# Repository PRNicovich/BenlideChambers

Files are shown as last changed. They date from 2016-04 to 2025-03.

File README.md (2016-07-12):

Benlide imaging chambers

Files and design instructions for 3D printed imaging chambers.

Work done by Ben Goodnow for EMBL Australia Node in Single Molecule Science at UNSW in conjunction with Rusty Nicovich and Kat Gaus.

PDF goes into more detail on comparison of these chambers to the commercially-available ones, as well as design rationale.  

Assembly instructions included in AssemblyNotes.txt.  For a single chamber, print off the base, main, and cover (optional) STL files.  Laser cut corresponding gasket. Then glue in magnets and you're ready to go!

Solidworks files available upon request (p.nicovich@unsw.edu.au).

End result - an imaging chamber that performs at least as well as a commercial one for microscopy for 1/50th the cost. 

New chambers are being added as we develop them.  These include new coverslip sizes as well as specialized applications, such as simultaneous imaging and electrochem manipulation.

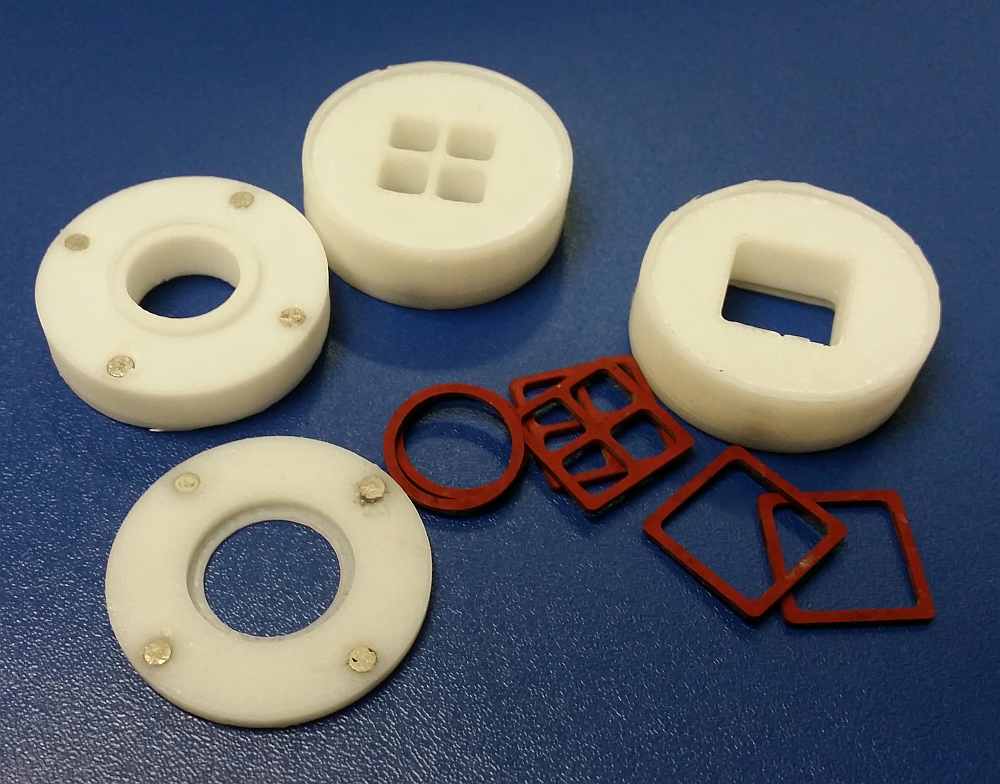
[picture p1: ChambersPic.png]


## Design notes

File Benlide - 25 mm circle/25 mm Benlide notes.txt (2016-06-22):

STL files are for two parts of chamber for 25 mm round coverslips. 

DXF file is for gasket for 25 mm round coverslips. 

Chamber parts require addition of 3 mm x 1 mm round Nd magnets.  These were sourced from similar vendors as given in master project instructions.  16 x N35 magnets required for each chamber.  Magnets are held in place with two-part epoxy.  Ensure that all magnets have the same North-South orientation so top and bottom rotational orientation is unimportant.  Check that any stray filament is removed from magnet recesses in print so that magnets can sit flush or just below the printed surface of the part.

Gasket is laser-cut from 1.25 mm thick silicone rubber sheet.  Material sourced from same vendor as given in master project instructions.

Care and some testing must be taken to ensure tolerances are met for a good seal with coverslip without excessive force and cracking.  Most critical dimension is the height of the recess in which the gasket rests on the chamber top.  If this is too tall there will not be a good seal; too short and there may be excessive force on the coverslip or poor binding between the top and bottom.  Also, top and bottom should have a good slip fit on their own.  This may require some adjustment of the diameter of the mating parts depending on the nozzle diameter and printer kerf if a different printer is used.

Printed on Zortrax M200 w/ Z-UltraT filament, 0.09 mm layer height, and medium infill.  As mentioned, some dimensions of the parts may need to be adjusted for different printers.  Each part is oriented on the print bed so that the magnet side is upright.  This prints the parts with no support material.  With a heated bed multiple parts can be printed at one time, otherwise single-part runs is recommended to avoid warping.

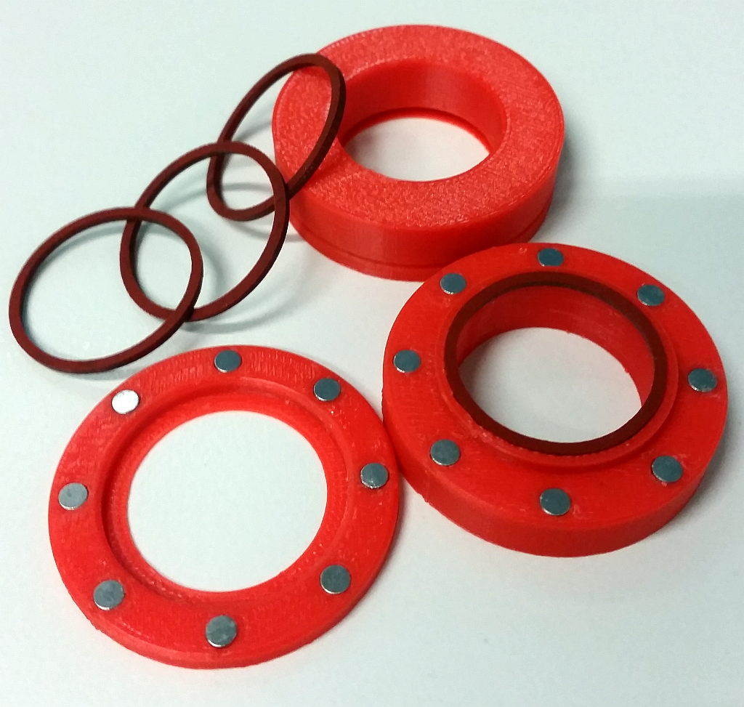
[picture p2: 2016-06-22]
Benlide - 25 mm circle/25 mm Benlide.png

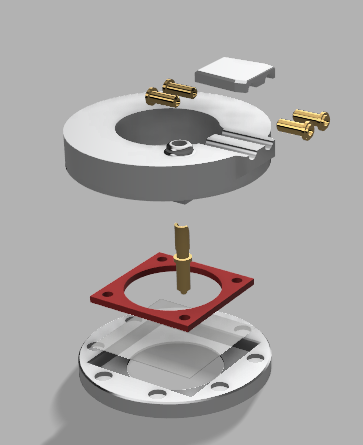
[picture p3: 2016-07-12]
ElectroBenlide/ElectroLideExplode.png

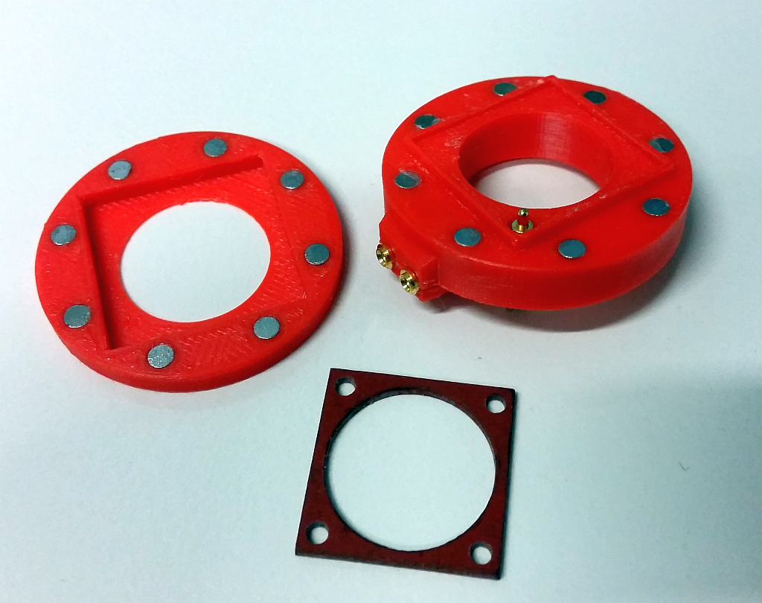
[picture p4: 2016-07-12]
ElectroBenlide/ElectroLide.png

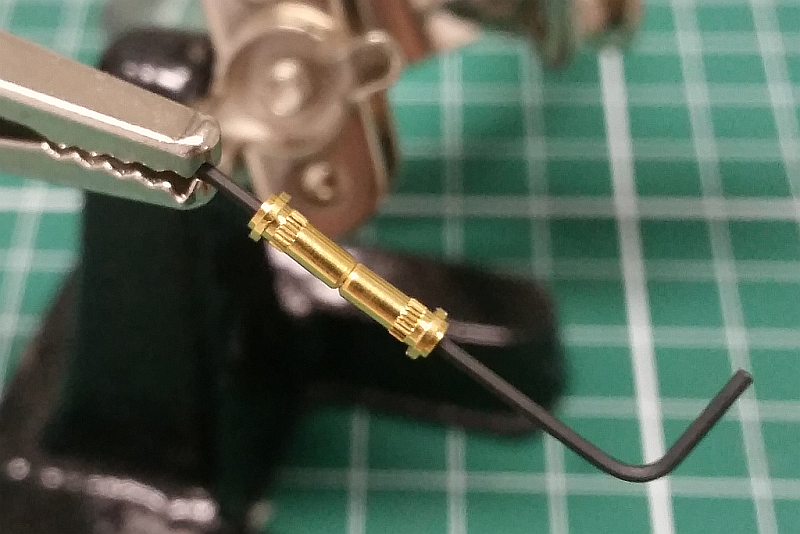
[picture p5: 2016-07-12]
ElectroBenlide/PCBSocketsOnStringer.png

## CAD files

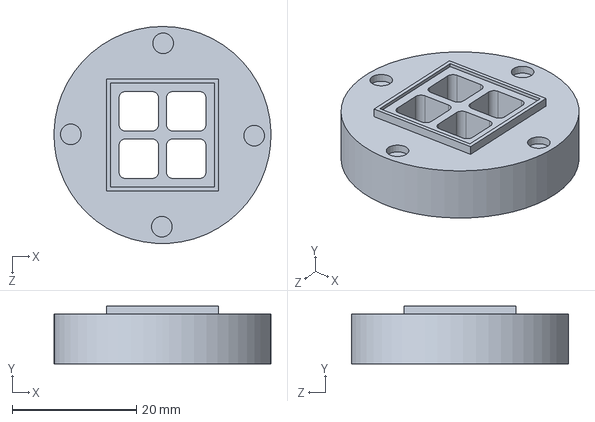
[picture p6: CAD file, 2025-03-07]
Benlide - Multi/CAD/MultiMain.SLDPRT
35.0 x 9.30 x 35.0 mm

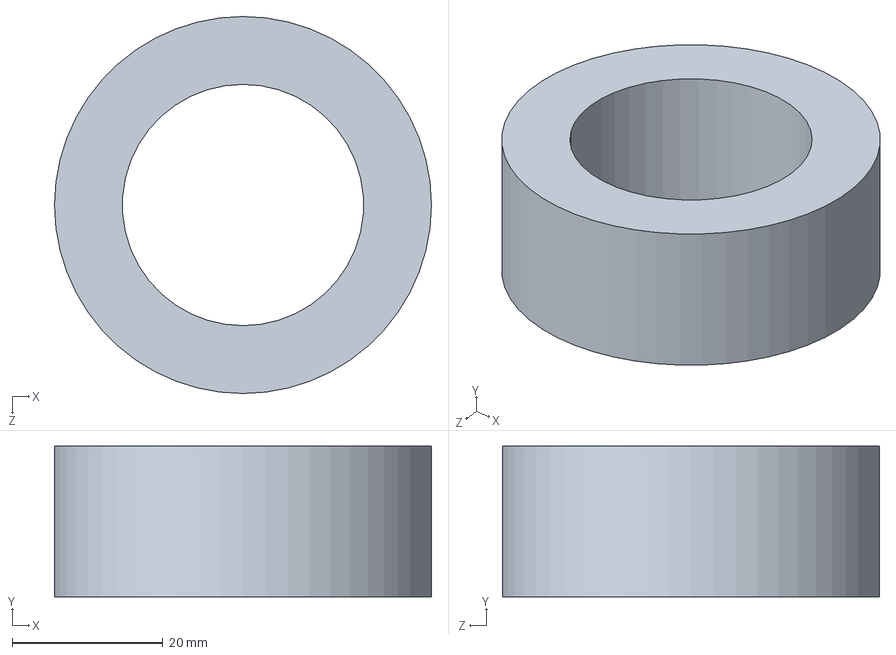
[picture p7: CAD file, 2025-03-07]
ProtoTest/CAD/Main Body.SLDPRT
50.0 x 20.0 x 50.0 mm

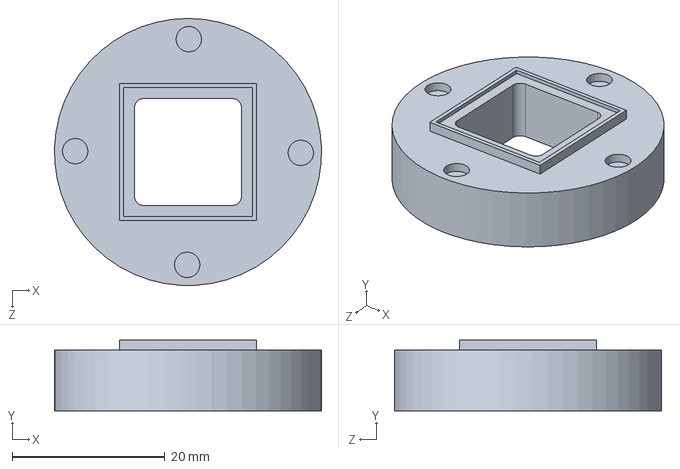
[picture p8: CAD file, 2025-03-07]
Benlide - 18 mm Square/CAD/SquareMain.SLDPRT
35.0 x 9.30 x 35.0 mm

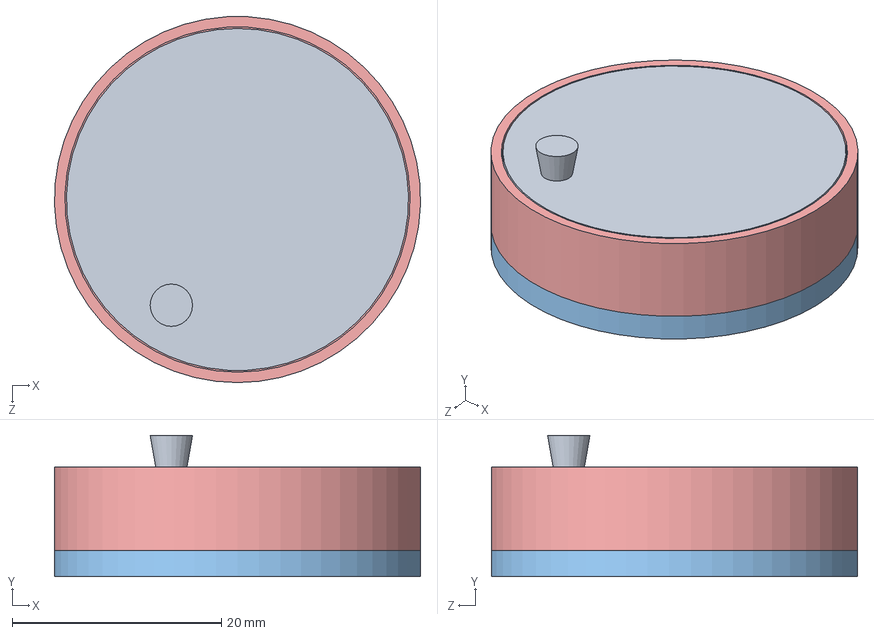
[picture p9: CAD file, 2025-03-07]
Benlide - 25 mm circle/CAD/Circle Assembly.SLDASM
35.0 x 13.5 x 35.0 mm
CircleGasket
CircleBase
CircleCoverslip
CircleMain
DiskMagnet x 8

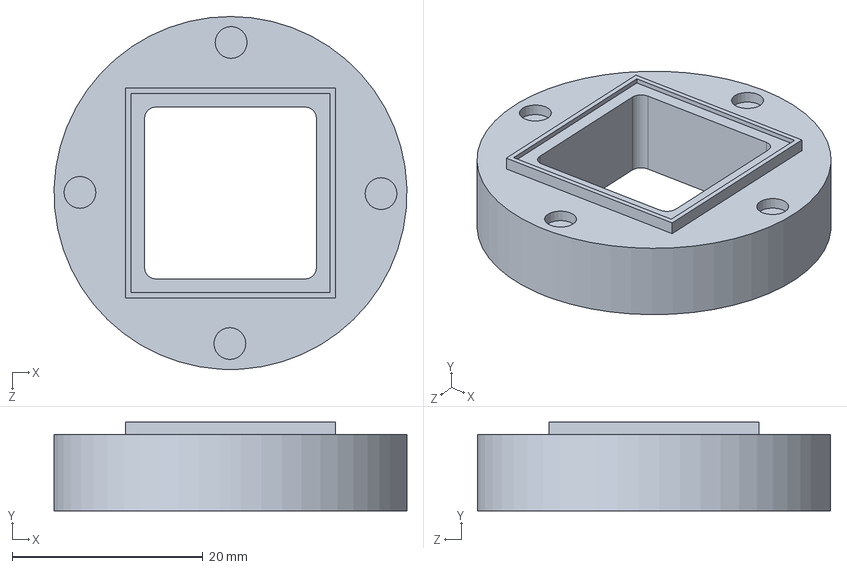
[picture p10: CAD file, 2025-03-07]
Benlide - Square - 22mm/CAD/SquareMain22.SLDPRT
37.0 x 9.30 x 37.0 mm

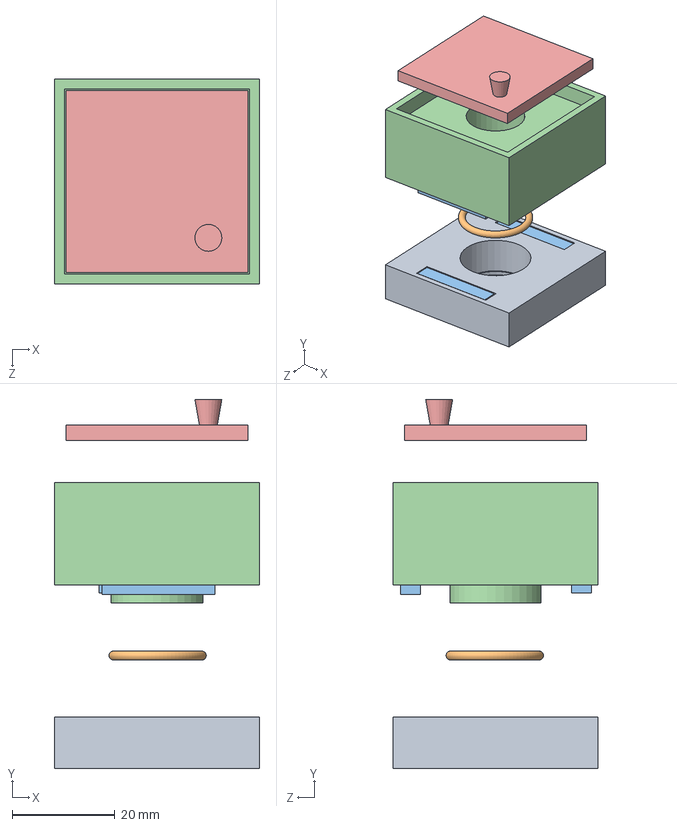
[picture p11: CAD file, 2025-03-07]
ProtoTest/CAD/Chamlide Assembly.SLDASM
40.0 x 72.0 x 40.0 mm
Bottom Plate
O-Ring
Magnet x 4
MainBod
TopCover^Chamlide Assembly

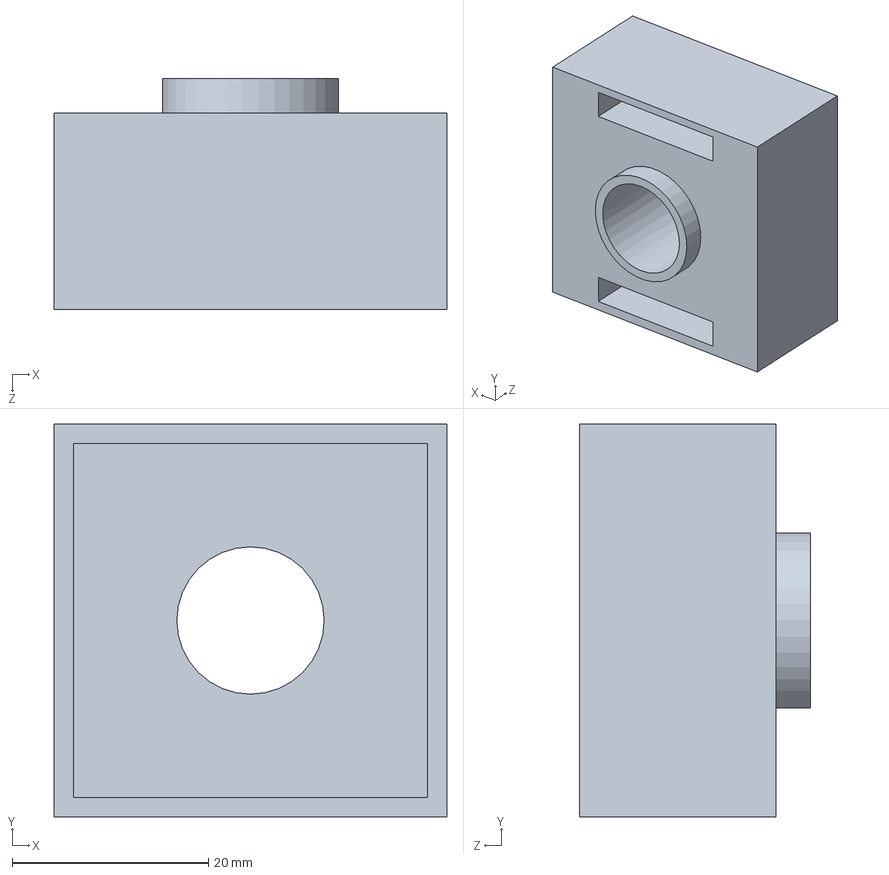
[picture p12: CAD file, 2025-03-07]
ProtoTest/CAD/MainBod.sldprt
40.0 x 40.0 x 23.5 mm

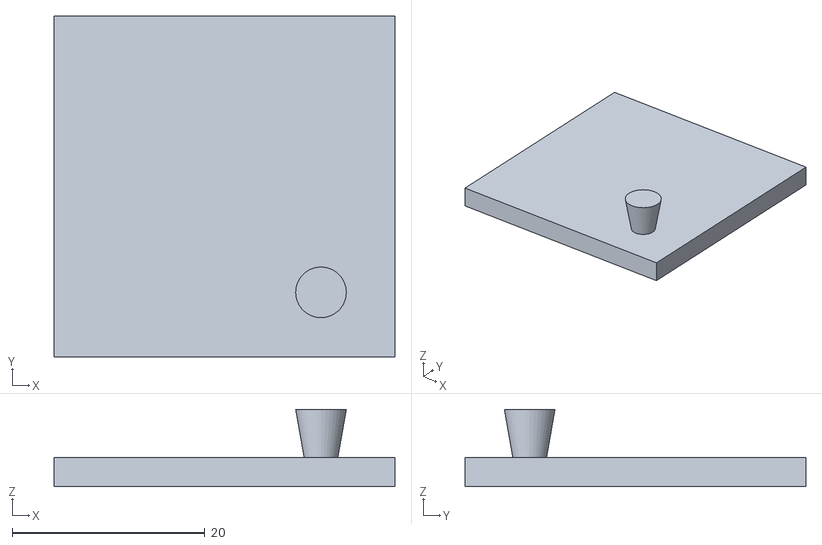
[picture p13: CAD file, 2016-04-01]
ProtoTest/CAD/TopCover^Chamlide Assembly.STL
35.4 x 35.4 x 8.00

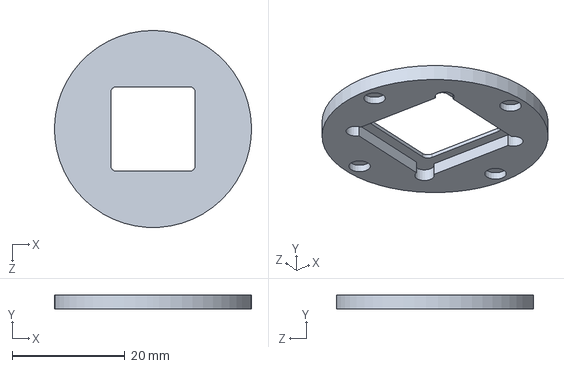
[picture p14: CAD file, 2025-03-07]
Benlide - 18 mm Square/CAD/SquareBase.sldprt
35.0 x 2.50 x 35.0 mm

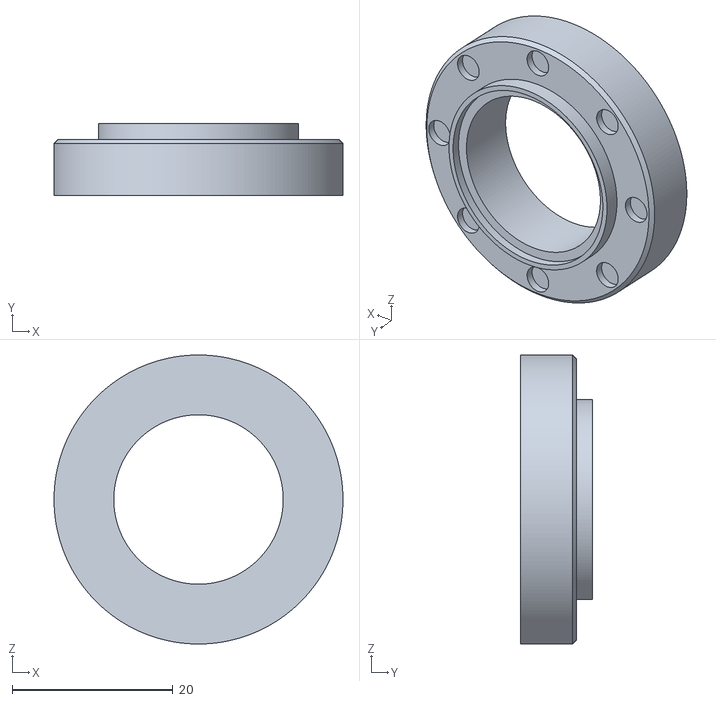
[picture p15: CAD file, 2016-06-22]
Benlide - 25 mm circle/25 mm top.stl
36.0 x 9.00 x 36.0

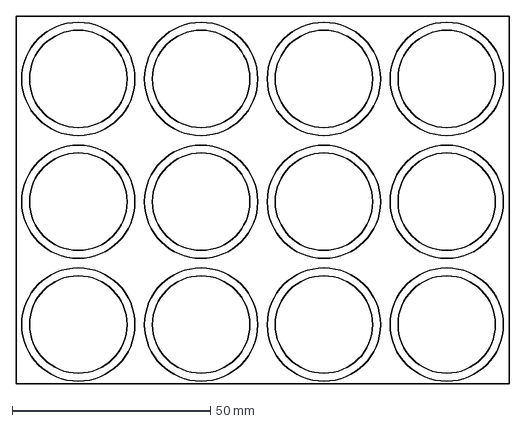
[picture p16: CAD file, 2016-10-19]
Benlide - 30 mm circle/30mmBenlideGasket.dxf
124.5 x 92.9 mm

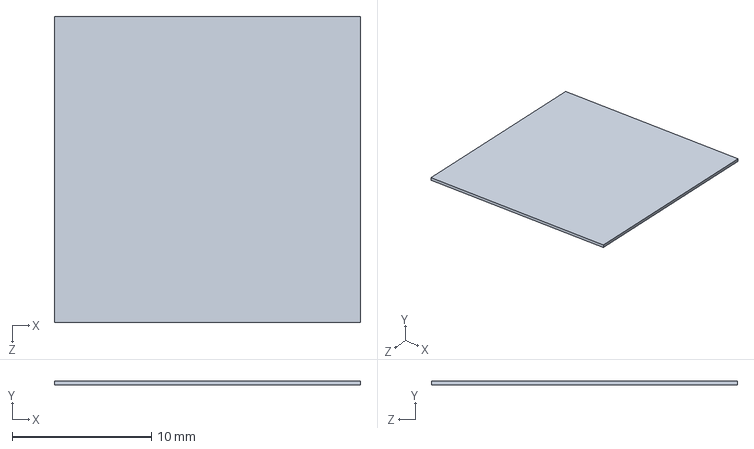
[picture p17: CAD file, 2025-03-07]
Benlide - Square - 22mm/CAD/SquareCoverslip22.sldprt
22.0 x 0.3 x 22.0 mm

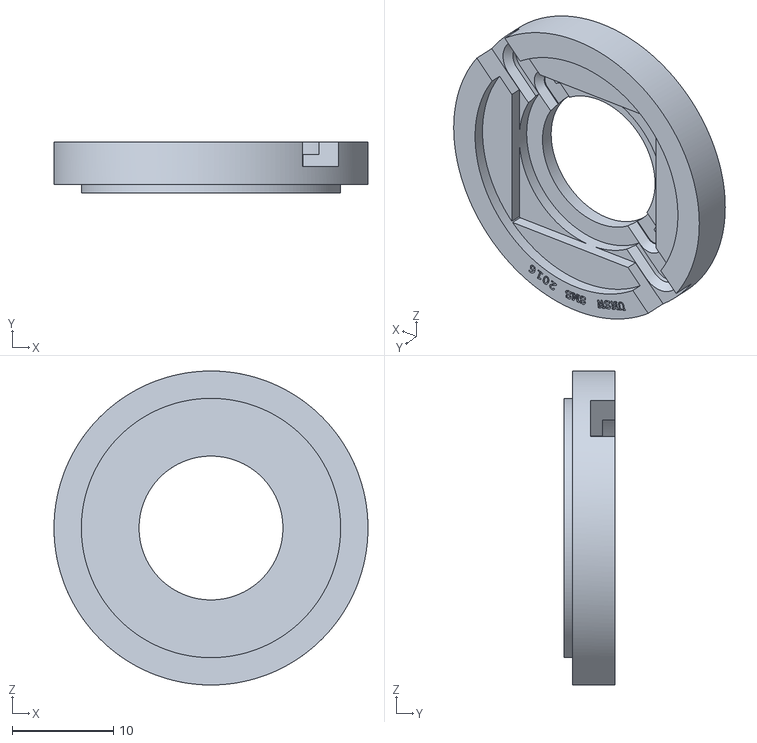
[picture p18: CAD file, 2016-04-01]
Coverslip Holder/CoverslipHolder18rnd18sq25sq.stl
31.0 x 5.00 x 31.0

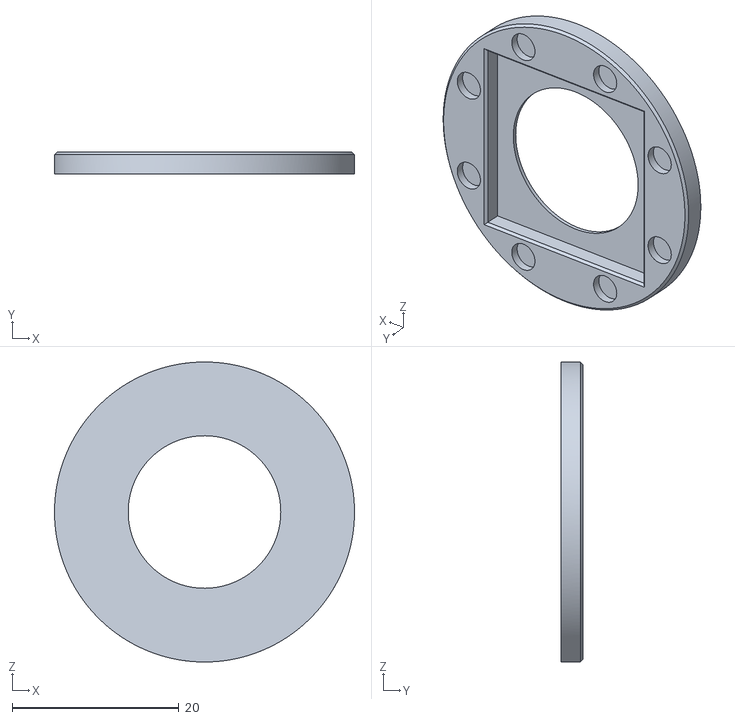
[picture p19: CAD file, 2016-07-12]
ElectroBenlide/ElectroLideBottom.stl
36.0 x 2.60 x 36.0

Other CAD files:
Benlide - 25 mm circle/CAD/CircleMain.SLDPRT
Benlide - 25 mm circle/CAD/CircleBase.sldprt
Laser Print Gasket/CAD/CircleGasket18mm.SLDPRT
Benlide - 18 mm Square/CAD/SquareBase.STL
Benlide - 18 mm Square/CAD/SquareCoverslip.sldprt
Benlide - 18 mm Square/CAD/SquareMain.STL
Benlide - 25 mm circle/25 mm bottom.stl
Benlide - 25 mm circle/25mmBenlideGasket.dxf
Benlide - 25 mm circle/CAD/ALLTop.SLDPRT
Benlide - 25 mm circle/CAD/ALLTop.STL
Benlide - 25 mm circle/CAD/CircleBase.STL
Benlide - 25 mm circle/CAD/CircleCoverslip.sldprt
Benlide - 25 mm circle/CAD/CircleMain.STL
Benlide - 25 mm circle/CAD/DiskMagnet.SLDPRT
Benlide - 30 mm circle/30 mm bottom.stl
Benlide - 30 mm circle/30 mm top.stl
Benlide - Multi/CAD/MultiBase.STL
Benlide - Multi/CAD/MultiBase.sldprt
Benlide - Multi/CAD/MultiMain.STL
Benlide - Multi/CAD/SquareCoverslip.sldprt
Benlide - Square - 22mm/CAD/SquareBase22.STL
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

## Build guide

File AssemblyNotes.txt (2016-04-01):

Chamlide Chamber Design
Benjamin Goodnow, February 2016

Enclosed:
Full report on the Custom Chamlide project (includes specific sources for materials)

Solidworks and STL CAD Files for 3D printing
	-18mm:Square, Circular, Multi. 22mm square. 1st prototype

Dxf files for Lasing Cutting silicone rubber gaskets
	-18mm Square, Circular, Multi, 22mm square

CAD Files for Other Projects (I.e. 3rd Arm and Laser Trigger Enclosure)

PRINTING
1.Using UP Plus 2 and UP Mini Printers. Heated platform+raft or enclosure support crucial in minimising warping. Use 1.75mm UP Premium ABS filament 
2.0.15mm layer height recommended for base, 0.2mm for main/top. 0.25-0.3mm should work
3.Up Software settings: "Fine" (slow-medium) speed for main body, "fast" (20mm^3/s+) for bottom
4.Print base with no support (so facing upwards), print main with support, top downwards, as a cut was made intended for a glass cover
5. Allow some time to coolbefore removing from platform (minimise warp)
6. Remove supports and sand/file any noticeable faults/imperfections
Complete
*Note to be careful priting multiple parts at once on the same printer. This effectivley halves your print speed, and so increases chances of warping. 
*Conversley this can be used to increases the "Fineness" of the print if required

CUTTING
1. Simply upload dxf file to laser cut program, align in cornerand set settings to 1mm thick rubber
2. Place silicone sheet in cutter. Make sure to align well and check focus
3. Run cut
4. Remove ash and surrounding silicone
Complete

ASSEMBLY
1. Need 8 disk 3x1mm rare earth magnets, 4 each half
2. First add small amount (very little needed) superglue to each magnet hole, then carefully place each magnet into each hole
***BE CAREFUL TO ENSURE POLARITY IS CORRECT***
3. Do so for both halves, making sure magnets are attracted to eachother
4. Allow glue to dry before connecting two halves
5. Sand any excess glue that has hardened over the tops of magnets
6. Place coverslip in baseplate with forceps
7. Place gasket in main/top half, stretching at corners (if needed) to fit tightly in extruded ring
8. Lower main onto Base, magnets will attract. Push together with fingers after to ensure attraction and gasket compression  
9. Add observation medium
Complete

CREATING VARIATION DESIGNS (I.E for 25mm coverslips)
-Simply edit Solidworks files as required, either by using the scale tool or by adjusting individual dimensions (Edit Sketch). 
-Gasket widths made need to be larger if outer radius increased, as will the very thin support for coverslip in base plate. 
-Body outer radius will have to be increased if through hole becomes too close to magnets

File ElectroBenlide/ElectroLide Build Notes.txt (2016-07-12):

Build notes for ElectroLide chamber for electrochem + imaging

-------------------------------------------------------------

Materials:

Make:
1 x ElectroLideBottom.stl
1 x ElectroLideTop.stl
1 x ElectroLideCap.stl
1 x ElectroLideGasket.DXF

Buy:
16 x 3x1  mm Nd disk magnets
1 x Mill-max 0854 spring-loaded pin ($2.27 AUD on Aussie element14, pt no 2065655)
4 x Harwin H3169-05 PCB socket ($1.27 AUD, element14 pt no 1617250)
5 minute epoxy or other appropriate adhesive 

The ElectroLide chamber is designed to allow for simultaneous imaging and electrochemical measurements through a 22 mm square ITO-coated coverslip.  A vertical pogo pin provides a spring-loaded contact to the top surface of the coverslip for an electrical connection that is convenient to access.  Two more pass-through contacts allow junctions between additional electrodes or connections to the buffer solution.  

Printing was done on a Zortrax M200 with a 0.09 mm layer height and medium infill in Z-UltraT.  Orientation is important, with the top and bottom pieces printed magnet side up and the cap flat side down.  

Gasket is laser cut from 1.25 mm silicone rubber sheet.  The rubber burns in a sooty flame, so there's some clean-up to do.  A sonication in ethanol does a good job removing the residual soot.

The tolerances for these fits are a bit tighter than the other chambers to have a good seal with the gasket.  It's a good idea to start with a printer that has a high amount of precision in the z axis (90 um layer height used here).  Still, there is some clean-up that's needed after printing.  A sharp razor blade is the best tool for this. The area to focus on is the gasket seat locations on the chamber top.  After a go on my printer, these needed to be trimmed down to fit easily within the bottom and to allow the gasket to seat effectively.  

The pogo pin sits with the pin point just proud of the gasket.  Too tall and it encourages leaking.  You may need to test fit the pin in place before gluing to double-check that this z position is correct.  Fit in the raw print is tight, but the pin itself can be used as a reamer to open the hole to final size.

The pass-through pins are a pair of PCB sockets soldered together butt-to-butt.  Putting them on a stringer (I used a ~1 mm hex key) works well to hold them in place for this operation (see pic in repo).  It's actually easier with *two* stringers, as you can really only thread a socket on in one direction.  But if you have a socket on a stringer, you can pass it to the other in the "wrong" direction by butting the stringers together and sliding the socket over to the other one. A bit of spatial reasoning will get you the two sockets on the same stringer with the correct orientation and a small bit of solder holds them together. These accept 1 mm thick wire (18 AWG) when picking out electrode connections.

Assembly involves gluing in the magnets (make sure they all point the same way!), the pogo pin, the butted-together socket pairs, and then the cap piece on top.  I held it all together with 5 minute epoxy which works well. 

Assembled chambers should be tested for leaks and electrical contact before you commit to an experiment.

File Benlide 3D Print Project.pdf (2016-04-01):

## ACCESSIBLE

## AND

## LOW

## COST

## DESIGN

## AND MANUFACTURING

OF

## “CHAMLIDE”

## OBSERVATION CHAMBERS

## FOR

## MOLECULAR

## IMAGING

## SMS

## Initiative

## -‐ Gaus Lab Lowy

## Cancer

## Research

## Centre

## Benjamin

## Goodnow Supervisor:

## Rusty

## Nicovich February

2016

ABSTRACT

The

aim

of

this

project

was

to

replicate

the

Chamlide

Magnetic

Chamber

by

Live

Cell
Instrument

using

alternate,

cheaper

and

accessible

manufacturing

processes

and
materials.

The

purpose

of

the

chamber

is

to

allow

efficient

placement

of

observation
medium

over

a

sample and

coverslip

to

allow

for

molecular

imaging

in

a

microscope.
The

processes

used

to

create

this

chamber

would

include

CAD

design,

3D

printing
each half

of

the

chamber,

adhering

of

rare

earth

magnets

into

the

chamber’s
designed

cuts

and

finally

laser

printing

silicone

gaskets

for

waterproofing.
Prototypes

were

made

and

tested,

with

faults

in

waterproofing,

tolerance,

magnetic
force

and

warping

to

be

addressed.

A final

product

resulted,

along

with

custom
variations

in

chamber

shapes

and

sizes

depending

on

need.

The

final

microscopy
image

results

proved

successful

and

comparable

to

the

original

Chamlides,

whilst
the

estimated

savings

for

producing

ten

chambers was

over $5000AUD.

TABLE

OF

CONTENTS

1.

Introduction | 4
2.

Conceptual

Design

and

First

Prototype | 5
3.

Second

Prototype

– Addressing

Key

Faults | 6
4.

Results

and

Discussion

of

Final

Product | 10
5.
Conclusion | 11
6

Sources

for

Materials

and

Manufacturing | 12

1.

INTRODUCTION

Currently

the

UNSW

Single

Molecule

Science

initiative,

aimed

at

developing

and
applying

molecular

imaging

technologies,

use

a

product

called

Chamlide

(Live

Cell
Instrument

Corp

[LCI]

2015)

for

containing

a

sample

within

an

observation

medium.
The

system

is

comprised

of

two

halves (Figure

1):

an

aluminium

base

with

a

steel
ring

inset and

through

hole

for

light

to

pass,

and

in

the

centre

a

glass

coverslip

(of
varying

shapes)

is

placed.

The

top

half

is

a

larger

plastic

body

with

magnets

inset,
which connects

to

this

base

through

magnetic

force,

allowing

for

a

liquid
observation

medium

to

be

added

on

top

the

coverslip.

To

prevent

water

leakage, a
silicone

gasket

is

used

between

the

two

bodies.

Finally, a

glass

cover

can

be

placed
on

the

top

of

the

Chamlide.

The

overall

system

improves

on

other

chamber

designs
which

use

screws

or

complex

assemblies,

reducing

leakage

and

increasing

efficiency.

However,

the

primary

drawback

of

this

design

is

cost.

A

single

unit

is

priced

at
approximately

$380USD

(Quorum

Technologies

2014),

due

primarily

to

its

unique
patented

design

occupying a

niche

uncontested.

With

many

projects

occurring

in

the
SMS

labs,

and

different

shape

and

size

coverslips

used,

many

units

are

required.
Thus

a

lower

cost,

accessible solution

is

required

to

ensure

the

lab

has

immediate
access

to

a

full

range

of

chambers,

increasing

efficiency

and

practicality

during
experimentation.

The

product

does

not

have,

nor

require, high

cost

materials.

The
material

costs

would

be

less

than

$20USD.

What

perhaps

may

increase

expenses

is
precision.

As

such

the

aim

of

this

project

is

to

design

a

similar,

precise

chamber

for
accurate

molecular

imaging

that

could

be

made

with

readily

accessed

materials
using

innovative,

low

price

manufacturing

processes.

(Figure

1.

Exploded

view

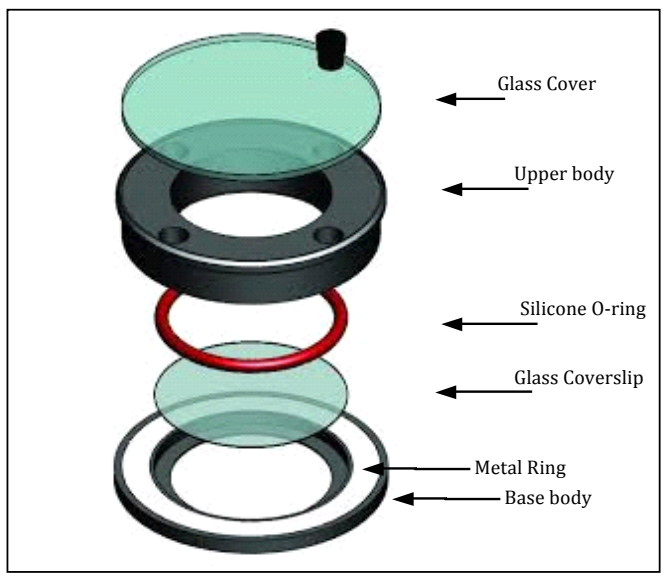
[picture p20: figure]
Glass; Cover; Upper; body; Silicone; O-‐ring; Coverslip; Metal; Ring Base

of

LCI's

Chamlide

CMB

commercially

available.

Quorum

Technologies

2014)

2.

CONCEPTUAL

DESIGN

AND

FIRST

PROTOTYPE

The

conceptual

design

of

the

chamber

followed

the

fundamentals

of

the

Chamlide,
with

the

key

constraints

and

solutions

transferable,

in

particular

the

use

of
coverslips,

waterproofing

for

the

observation

medium,

and

magnetic

connection

of
the

two

halves.

However,

two

key

changes

were

made:

no

glass

cover,

deemed

a
non-‐crucial

aspect

increasing

material

costs;

and

no

inset

steel

ring,

instead

utilising
magnets

in

the

base

just

as

the

top,

again

reducing

the

bill

of

materials

and
manufacturing

processes

required.

The

design

of

the

chamber's

plastic

body

underwent

multiple

iterations

in

order

to
achieve

a

refined

design,

with

problems

in

precision,

tolerance

and

material

choice
to

be

overcome.

The

flexibility

of

CAD

software

and

3D

printed

prototypes

allowed
for

an

efficient

iterative

process.

All

CAD

design

was

completed

in

Solidworks

2014
(Dassault

Systemes

2014)

and

the

manufacturing

of

the

body

used

a

mid-‐range

UP
Plus

2

Desktop

3D

printer

(UP3D

2015).

This

printer

utilised

1.75mm

ABS

filament,
a

high-‐temperature-‐resistant

and

durable

plastic,

suitable

for

the

range

substances
the

chamber

may

require,

and

suitable

for

use

in

an

autoclave.

A

kilogram

of

ABS
can

be

purchased

for

$50AUD

(with

one

chamber

requiring as

little

as

15g).

It

is

to
be

noted

that

PLA

(a

common

3D

Printing

material)

is

less

temperature-‐resistant
and

known

to

deform

at

higher

temperatures,

hence

the

preference of

ABS

(B
Tymrak

et

al.

2014)

The

first

prototype

printed

(Figure

2)

was

designed

primarily

around

an

18mm
round

coverslip

and

medium

sized

rectangular

block

(2.2x0.5x0.5cm)

ceramic
magnets,

chosen

due

to

low

price

and

high

accessibility

($5AUD

from

hardware
outlets).

Due

to

the

shape

and

size

of

the

magnets

a

cube

shape

was

required,
40x40x30mm.

(Figure

2.

CAD

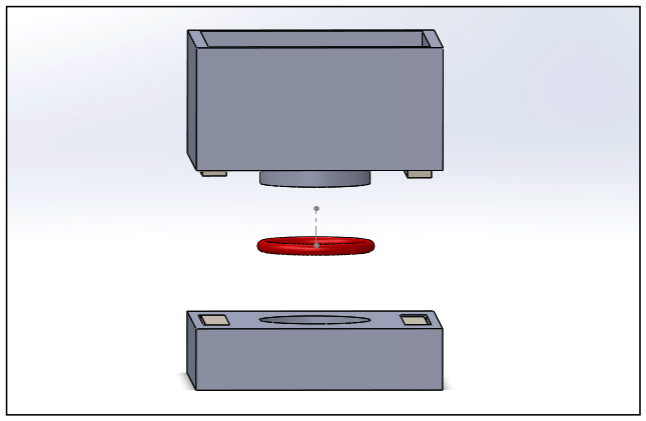
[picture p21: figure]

design

of

prototype

Chamlide

[note

the

top

of

the

upper body

had

a

cut

made

to

allow

for
the

possibility

of

a

glass

cover])

For

testing,

an

18mm

glass

coverslip

and

commercial,

common

silicone

o-‐ring

(via
hardware

outlet)

were

placed

using

forceps

in

the

base

half

successfully,

with
enough

clearance

to

be

carefully

lowered,

but

tight

enough

such

that

neither
component

shifted.

The

magnets

could

also

be

inset

easily,

with

flush

edges

to

allow
uniform attraction,

and

kept

in

place

with

no

glue

required.

However,

when

the

upper

and

base

parts

were

connected,

it

was

found

the

size

of
the

magnets

provided

a

strong

attractive

force,

far

stronger

than

the

steel-‐to-‐magnet
combination

of

the

LCI

system.

Consequently,

the

coverslip

was

shattered.

The
diagnosis

of

this

fault

led

to

multiple

possibilities.

Firstly,

magnets

were

only

placed
on

two

of

the

four

sides,

leading

to

higher

pressure

on

only

these

sides,

resulting

in

a
bending

moment

on

the

coverslip.

Secondly,

and

likely

the

largest

contributor,

the
magnet

size

was

simply

too

large

for

a

chamber

of

this

size,

creating

an
overwhelmingly

stressful

load

on

the

coverslip.

Thirdly,

the

durometer

(hardness)
of

the

o-‐ring

was

high,

at

70,

meaning

more

force

was

required

to

compress

it

and
hence

more

force

transferred

to

the

coverslip.

Another

possible

issue

was

also

detected

when

analysing

the

chamber's
implementation.

The

square-‐shaped

and

4

cm^2

footprint proved

to

be

unable

to

fit
within

some

of

the

microscope

systems

used

in

the

SMS

Labs.

Furthermore,

the
distance

(5mm)

between

the

bottom

of

the

base

section

and

the

coverslip

reduced
flexibility

in

the

minimum

distance

the

objective

lens

could

be

to

the

sample.

In
addition

to

this,

the

base

and

inner-‐cut

where

the

coverslip

rested

were

not
completely

flat

due

to

warping

during

the

3D

printing

process.

The

coverslip

must
be

parallel

with

the

lens in

order

to

not

produce

imaging

errors; hence

reducing

this
warp

is

crucial

to

the

design's

precision

and

reliability.

3.

SECOND

PROTOTYPE

-‐ ADDRESSING

KEY

FAULTS

Consequently

all

issues

were

to

be

addressed

in

the

second

iteration

of

the

design
(Figure

3).

The

most

immediate

change

was

the

magnet

choice.

The

large

ceramic
magnets

were

changed

for

much

smaller,

3x1mm

disk-‐shaped

rare

earth magnets.
These

were

inset

into

the

3D

printed

body

by

making

four

cylindrical

cuts

(in

CAD)
about

the

circumference,

allowing

a

clearance

of

0.2mm

to

be

tolerant

of

the

lower
accuracy

in

finer

3D

printed

details.

The

small

size

meant

a

lower

coefficient

of
friction,

requiring

the

magnets

to

be

glued

into

the

cuts,

simply

using

a

small
amount

of

store-‐bought

superglue.

Care

was

taken

in

ensuring

all

four

magnets

in
the

each

half

of

the

body

had

the

same

polarity

outwards,

and

in

ensuring

the
magnets

in

the

opposite

half

were

the

opposite

polarity

for

magnetic

attraction.
Some

sanding

was

required

if

glue

built

up

over

the

magnet,

meaning

the

two
chambers

would

not

connect

uniformly.

A

fine

balance

had

to

be

made

for

the
magnet

inset depth,

as

too

deep

reduced

the

strength

of

the

attraction,

yet

too
shallow

and

the

magnet/glue

may

protrude.

Both

problems

lead

to

a

situation

in
which

the

o-‐ring

did

not

seal

and,

when

tested

with

water,

there

was

leakage

from

the

chamber.

A

prototype

using

six

magnets

was

also

tested,

no

significant

benefits
were

observed

and

as

such

it

was

more

cost

effective

to

use

four.

(Figure

3.

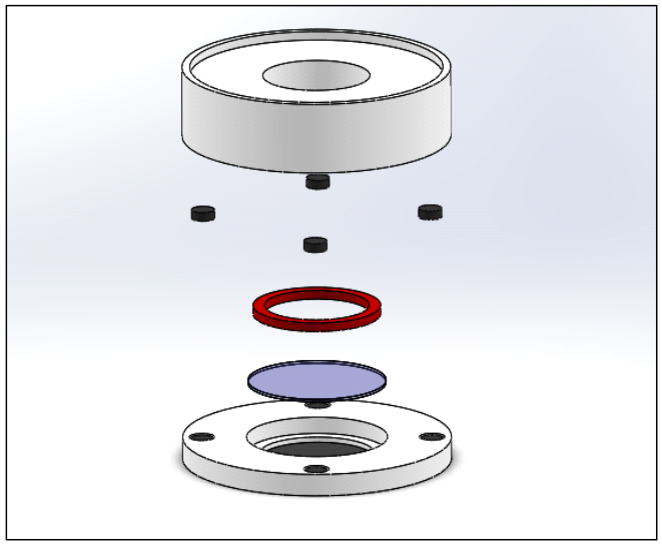
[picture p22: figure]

Exploded

view

of

the

second

iteration.

From

top

to

bottom:

the

upper

ABS

half

[*note
cylindrical

extrusion

cannot be

seen],

4

rare

earth

magnets

evenly

spaced,

silicone

gasket,

glass
coverslip,

ABS

base

half

with

inset

magnets)

With

the

new

magnets,

a

body

designed

for

an

18mm

coverslip

could

now

be
reduced

to

a

35mm

disk

footprint,

fitting

for

microscope

platforms

and

reducing
plastic

cost

in

printing.

The

depth

of

the

chamber

(both

halves)

was

also

reduced.
Furthermore,

this

smaller,

lighter

design

led

to

reduced

warping.

Warping

during
the

3D

printing

process

is

caused

when

the

outer

and

lower

(older)

layers

of

a

solid
begin

to

cool

before

the

interior

and

newer

layers,

which

are

more

thermally
insulated.

Consequently,

in

a

smaller

design,

there

is

less

time

for

the

solid

to

cool
un-‐uniformly.

Nevertheless,

to

ensure

minimal

warping,

a

heated

platform

(85C)
was

used,

along

with

an

enclosure

to

heat

the

air

around

the

piece,

and

the

print
speed

set

to

fast

(up

to

30mm^3/s)

for

the

base

half.

A

“raft” support

structure

was
also

used,

in

which

a

layer

of

ABS

is

printed

first

with

a

lower

nozzle

height

to

press
the

plastic

firmly

into

the

base

plate.

The

inner-‐cut

(supporting

the

coverslip)

of

the

base

section

was

also

reduced

from
5mm

to

a

minimal

thickness

of

0.6mm.

Multiple,

incremental

prototype

prints

were
carried

out

to

test

this,

with

anything

thinner

found

to

be

too

fragile

to

be

removed
from

the

support

raft

in-‐tact.

A

print

layer

thickness

of

0.15mm

was

required

in
order

to

achieve this.

The

final

problem

to

be

resolved

was

the

waterproofing

gasket.

The

upper

chamber
half

has

a

cylindrical/ring extrusion

(Figure

4)

with

an

inner

cut

(along

with

the

through-‐hole)

for

a

gasket

to

lie

within.

This

extrusion,

in

combination

with

the

base
cut

for

the

coverslip,

required

multiple

prototypes

in

order

to

determine

both

the
ideal

width

and

depth.

A clearance

of

0.5mm

(generally

0.2mm

is

considered
tight/unmoveable

whilst

0.4mm

used

for

kinetic

connections)

was

used

in

the

base
cut

for

the

coverslip,

to

ensure

ease

of

placement

while

allowing

only

very

slight
movement.

The

extrusion

then

had

to

have

an

0.4mm

clearance

of

the

base

cut

to
ensure

friction

did

not reduce

the

force

from

the

magnetic

system.

Finally,

the
gasket

would

sit

within

this,

and

could

not

have

an

inner

radius

below

14mm

as

this
would

reduce

the

viewable

sample

area.

It

also

needed

to

protrude

past

the
extrusion

to

ensure

that

it

was

in

contact

with

the

coverslip

(whilst

in

compression),
instead

of the

plastic

(for

the

coverslip

would

shatter).

Thus,

there

was

a

very

small
margin

for

error

in

this

part,

and

as

such

standard

commercial

o-‐rings

of

low
durometer

did

not

have

the

variety

to

allow

for

a

precise

size.

This

was

augmented
when

considering

the

need

for

square

and

multiple-‐chamber

gaskets

to

enable

other
chamber

designs.

Multiple

alternatives were

subsequently

considered,

including
professional

moulding or

purchasing

replacement

O-‐rings

from

LCI.

Both

options
proved

to

be

highly

cost-‐ineffective,

moulding only

effective

for

high

volume

(over
500

gaskets),

and

LCI

maintaining

a

high

price

for

a

single

replacement

gasket.

(Figure

4.

Red

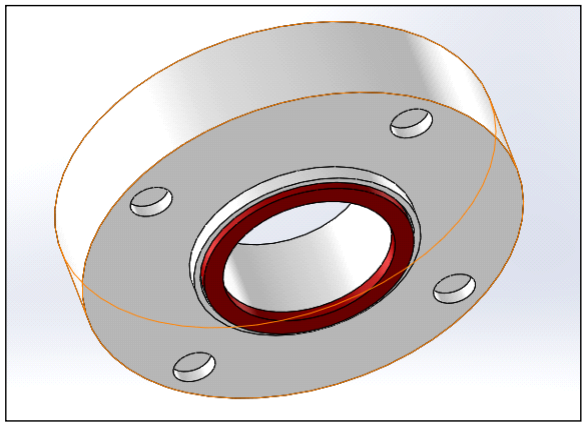
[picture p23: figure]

silicone

gasket

lies

within

the

shallow

extruded

cylinder

of

the

3D

printed

body's

top
half.

Note

how

the

gasket

slightly

protrudes)

Laser

cutting

using

silicone

rubber

sheets

was

the

chosen

alternative.

It

is

a
relatively

low-‐cost

manufacturing

process

and

material

for

a

cut

this

size.

The
gaskets

were

designed

in

Solidworks

and

exported

to

a

useable

format

for

the

Laser
Cutter

(Dxf),

with

particular

care

taken

to

ensure

the

kerf

of

the

laser

(in

this

case
0.15mm)

was accounted

for,

as

precision

was

key.

Silicone

gaskets

in

circular,
square

and

multi-‐chamber

shapes

(Figure

5)

were

successfully

cut,

using

1mm
silicone

sheets

with

50

durometer.

Despite

an

unusual

flame

caused

by
vulcanisation

of

the

rubber,

they

were

of

the

required

precision

and

hardness.

(Figure

5.

Three

forms

of

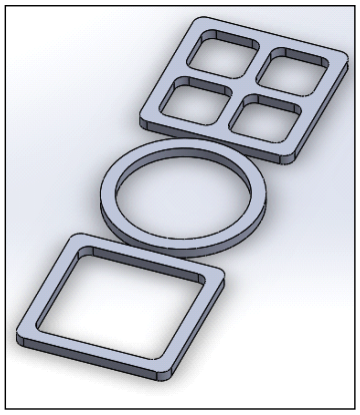
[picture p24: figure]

laser

cut

silicone

gaskets.

From

top

to

bottom:

multi-‐chamber,

circular

and
sqaure.

Each

are

1mm

thick

and

18mm

wide/diameter)

Furthermore,

during

3D printing

very

small

nodules

or

bumps

can

occur

when

the
3D

printer

retracts

and

changes

directions

during

a

print.

In

a

fine

detail

part,

this
effect

can

lead

to

larger

error

than

anticipated.

Slight

sanding

was

used

in

a

few
cases

(on

corners

particularly),

however

after

running

nozzle

height

calibrations
and

incrementally

altering

settings

in

the

printer

(i.e.

increasing

retraction,

setting
to

a

slower

print

speed)

later

designs

printed

very

well.

As

insurance,

the

gaskets
were

made

slightly

smaller

to

fit

regardless of

nodules,

and

in

the

case

where

there
were no

imperfections; light

stretching

can

be

used

to

ensure

the

correct

fit.

In
doing

this

there

is

a

greater

tolerance

to

both

the

3D

printing

and

O-‐ring

processes.

4.

RESULTS

AND

DISCUSSION

OF

FINAL

PRODUCT

Having

corrected

the

critical

faults

of

the

original

prototyped

design,

and
incrementally

refined

the

chamber

to

a

precise

size

and

fit,

the

second

design
proved

to

be

the

final

product.

The

3D

printed

chamber

halves

locked

magnetically
together

uniformly,

such

that

the

laser

cut

gasket

was

successfully

compressed
against

the

coverslip,

with

no

leakages

occurring.

Furthermore,

the

design

footprint
was

refined

and

could

be

successfully

tested

in

the

lab,

producing

clear

images
comparable

to

LCI's

Chamlide,

proving

there

was

minimal

warping,

with

the
coverslip

both

parallel

and

at

an

acceptable

distance

to

the

objective

lens.

Having
successfully proved

the

viability

for

an

accessible,

low

cost

design,

multiple
alternate

designs

could

be

produced

from

this

base

product.

This

included

a

square
and

multi-‐chamber

design

(Figure

8)

along

with

a

larger,

21mm

coverslip

design.
The

options

and

variety

are

vast

with

each

component in

the

manufacturing

process
providing

great

flexibility.

Table

1

shows a

cost

analysis

of

the

design,

including

materials

and

manufacturing.

MATERIALS | COST (AUD)
ABS UP Premium* Filament -‐ 7.5g *Less “nodules” than cheaper filaments and less warping | $0.6 ($35/500g)
8 Rare Earth Disk Magnets | $1.32 ($16.5 for 100)
Super Glue | $2
Silicone Gasket | $0.1 ($10 Silicone sheet, makes 100)
MANUFACTURING | COST (AUD) *Estimation
3D Printing | Desktop printer is of small size and commercially available to all. Running costs is only ABS plastic. $1240 (variable) for printer, however sites such as 3D Hubs allow for community-‐based printing services charging for amount of ABS and a small service charge ($10-‐$15 per Chamber)
Laser Cutting | Used Universal 24 by 18 inch laser Cutter. Would be too costly to buy, however Laser Cutting services are also available. Most companies charge $3 per unique part and $1 per replica, however this is lowered for size, simplicity and material thickness. Gaskets would hence cost less than $1 each to print. Most companies charge $25 minimum however.

(Table

1.

Cost

Estimations

for

both

material

and

manufacturing)

It

is

clear

from

this

analysis

the

prices

are

minimal. For

a

higher

volume

of
Chambers

the

price

will

inevitably

reduce

per

unit.

For

fabricating

only

a

single
Chamber

the

maximum

cost

(assuming

printing

services

are

used)

would

be

$103.5.
AUD.

For the SMS Lab, ten were

made,

utilising

the

free

UNSW

services

for
manufacturing.

This

was

at

an

approximate

cost

total

(given

a

minimum

500g

of

abs
can

be

bought)

of

$63.5

for

all

ten,

or

$6.35AUD

each.

All

prototypes

could

also

be
made

enclosed

within

this

budget.
As

of

late

February,

$380USD

equates

to

$514AUD,

the

price

of

a

single

Chamlide
CMB

Chamber

from

LCI

(via

Quorum

Technologies).

Thus

the

Lab

saved

$5076.5,
whilst

further opening

opportunity

for

custom

designs

and

sizes

as

required.

In

terms

of

areas

of

improvement,

the

design

is

not

as

high

a

quality in

terms

of
finishing

and

precision

as

the

Chamlide.

The

gaskets

may

require

slight

adjustment
through

stretching,

and

some

friction

may

occur

when

connecting

the halves,
requiring

the

halves

to

be

pressed

together

lightly

to

ensure

waterproofing.
Aesthetically

they

are

marginally

rougher.

Care

must

be

taken

in

gluing

the

magnets
in

particular

to

ensure

a

refined

visual

and

functional

appeal.

Cleaning

may

also

be
more

difficult,

with

the

more

porous

ABS

layers

and

imperfections

in

printing
leading

to

grooves

and

pits

which

could

hold

substances.

The

magnet

cuts

are

also
not

completely

sealed

off,

a

recommendation

for

future

improvement,

achievable

by
using

an

ABS

and

acetone

“slurry”

to

back-‐fill

after

magnet

placement.

5.

CONCLUSION

The flexibility

of

CAD

design

software

along

with

the

accessibility

and

low

cost

of
manufacturing

through

3D

printing

and

Laser

Cutting

are

key

advantages

in

the
chamber’s

design.

It

will allow

lab

workers

the

option

to

order

an

alternate

design
required

for

their

project

and

have

it

available

with

little

time

and

cost,

far
surpassing

the

less

flexible

and

high

cost

Chamlide.

Above

all,

the

custom

chamber
achieves

this

without

reducing

imaging

quality.

6.

SOURCES

FOR

MATERIALS

AND

MANUFACTURING

CAD:

http://www.solidworks.com/

Silicone

rubber

sheets:

http://www.ebay.com.au/itm/301621017741 Magnets:

http://aussiemagnets.com.au/product/-‐-‐3mm-‐x-‐-‐-‐-‐1mm-‐Disc-‐%28Rare-‐ Earth%29-‐-‐%28Pack-‐of-‐100%29.html

Premium

UP

ABS

Filament: http://store.3dprintingsystems.com/filaments/up-‐abs UP

Plus

2

3D

Printer: http://store.3dprintingsystems.com/up-‐plus-‐2-‐3d-‐printer 3D

Hubs

for

Print

Service:

https://www.3dhubs.com/

Universal

Laser

Cutter:

http://www.ulsinc.com/en-‐au/products/pls475/Laser

Cutting

Service:

https://onlinelasercutting.com.au/

Original

Chamlide:

http://www.chamlide.com/
Chamlide

via

Quorum:

http://www.quorumtechnologies.com/index.php/2014-‐06-‐19-‐13-‐10-‐00/2014-‐06-‐19-‐13-‐15-‐39/environment-‐chambers/chamlide-‐cmb-‐for-‐ 18mm-‐round-‐coverslips-‐1-‐detail

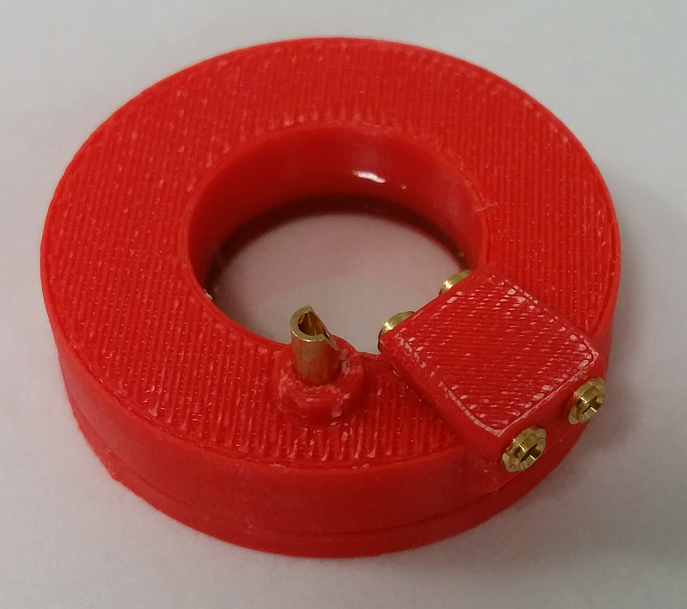
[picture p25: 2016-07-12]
ElectroBenlide/ElectroLideAssembled.png

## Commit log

2016-04-01 Initial commit.
    [ALLTop.STL, Bottom Plate.STL, CircleBase.STL, CircleGasket.DXF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]
2016-04-01 Added pic of chambers.
2016-06-22 Added 25 mm round chamber and started file name changes
    [25 mm bottom.stl, 25 mm top.stl, 25mmBenlideGasket.dxf, ALLTop.STL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]
2016-06-22 Rename folders.
    [ALLTop.STL, CircleBase.STL, CircleMain.STL, MultiBase.STL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]
2016-06-22 Added missing DXF files from renaming.
    [CircleGasket18mm.DXF, CircleGasket25mm.DXF]
2016-07-12 Added ElectroLide folder and files.
    [ElectroLideBottom.stl, ElectroLideCap.stl, ElectroLideTop.stl]
2016-10-19 Added files for 30 mm round chamber.
    [30 mm bottom.stl, 30 mm top.stl, 30mmBenlideGasket.dxf]
2025-03-07 Add CAD files
    [ALLTop.SLDPRT, ALLTop.STL, Bottom Plate - Copy.SLDPRT, Bottom Plate.SLDPRT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]
